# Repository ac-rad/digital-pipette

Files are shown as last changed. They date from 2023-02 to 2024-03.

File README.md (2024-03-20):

# Digital pipette


This repository contains CAD files and programs for [Digital pipette: Open hardware for liquid transfer in self-driving laboratories](https://doi.org/10.1039/D3DD00115F)

## Demo Video
https://user-images.githubusercontent.com/29328746/236104835-9dc766c4-92dd-4aab-9998-5ebd59588d73.mp4

## Bill of materials
| Item | Quantity | Description | Note |
| --- | --- | --- | --- |
| Linear actuator | 1 | Actuonix L16-100-63-6-R | https://www.actuonix.com/l16-100-63-6-r |
| DC 6V power supply | 1 | DC Linear Actuator Power Supply* | https://www.actuonix.com/dcpowersupply |
| Arduino | 1 | Arduino Uno Rev3** | https://store-usa.arduino.cc/products/arduino-uno-rev3 |
| Syringe | 1 | NORM-JECT Luer Solo (10 mL) | https://us.vwr.com/store/product/4646293/norm-ject-luer-lock-sterile-syringes-air-tite-products |
| Short screws & nuts | 3  | M3 10 mm screws and M3 nuts were used | |
| Long screw & nut | 1 | M3 20 mm screw and M3 nut were used | |

Basic electronic Parts to build a circuit (e.g. breadboard, cables, soldering iron, etc.) are not included in the list.

\* Any other DC 6V power supply should work.

** Any other Arduino-compatible boards should work.

## Electric circuit


Although it is not drawn explicitly, please make sure that the GND of Arduino and DC 6V power supply are connected.

### Example setup
You can connect with Arduino, the linear actuator, and the 6V power using jumper wires and alligator cables. This setup works for development, but it is not recommended for production since cables get easily disconnected.



Soldering wires is recommended for production to make connections more stable. My example using a PCB prototyping board is shown below.



## Build instruction
### Step 1
Prepare items shown in the bill of materials. Print the [platform](https://github.com/ac-rad/digital-pipette/blob/main/design/stl/platform.stl), [plunger holder](https://github.com/ac-rad/digital-pipette/blob/main/design/stl/holder.stl) and [syringe cover](https://github.com/ac-rad/digital-pipette/blob/main/design/stl/cover.stl) with a 3D printer. The length of the linear actuator should be adjusted before building by using an Arduino and the provided code. A screwdriver and pliers are helpful to tighten screws.



### Step 2
Connect the linear actuator and the plunger holder with a short screw and a nut.

https://github.com/ac-rad/digital-pipette/assets/29328746/378bcaca-c717-46af-9cfb-5fd15bf9850b

### Step 3
Connect the linear actuator and the platform with plastic parts shipped with the actuator, screws (short and long), and nuts.

https://github.com/ac-rad/digital-pipette/assets/29328746/e1789dd6-4c45-4c4c-84f6-89d388aaab22

### Step 4
Connect the syringe plunger with the plunger holder. Fasten the syringe with the platform and the syringe cover.

https://github.com/ac-rad/digital-pipette/assets/29328746/42ebc0b9-3168-43e8-8522-d95415921b36

### Step 5
Connect the linear actuator with the electric circuit.

## Source code
[src](https://github.com/ac-rad/digital-pipette/tree/main/src) directory contains an example code to operate the digital pipette.
- `pipette.ino` is an example Arduino sketch
- `controller.py` is an example Python code to send commands from PC to the Arduino

## Citation
If you find this useful in your research, please consider citing as below.

```
@article{yoshikawa2023digital,
  author = "Yoshikawa, Naruki and Darvish, Kourosh and Vakili, Mohammad Ghazi and Garg, Animesh and Aspuru-Guzik, Al{\'a}n",
  title = "Digital pipette: open hardware for liquid transfer in self-driving laboratories",
  journal = "Digital Discovery",
  year = "2023",
  volume = "2",
  issue = "6",
  pages = "1745-1751",
  publisher = "Royal Society of Chemistry",
  doi = "10.1039/D3DD00115F"
}
```

## License
The pipette is licensed under the [Creative Commons Attribution 4.0 International License][cc-by].

[][cc-by]

[cc-by]: http://creativecommons.org/licenses/by/4.0/
[cc-by-image]: https://i.creativecommons.org/l/by/4.0/88x31.png

The source code is licensed under the MIT license.

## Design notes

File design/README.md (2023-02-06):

# Design files for digital pipette
- `f3d/` contains Fusion 360 model in F3D format
- `stl/` contains 3D model in STL format.

`platform_upper` and `platform_bottom` are designed for 3D printers with small printable area.

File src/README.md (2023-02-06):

# Souce code for the digital pipette

- `pipette.ino` is an Arduino sketch
- `controller.py` is an Python example to send commands from PC

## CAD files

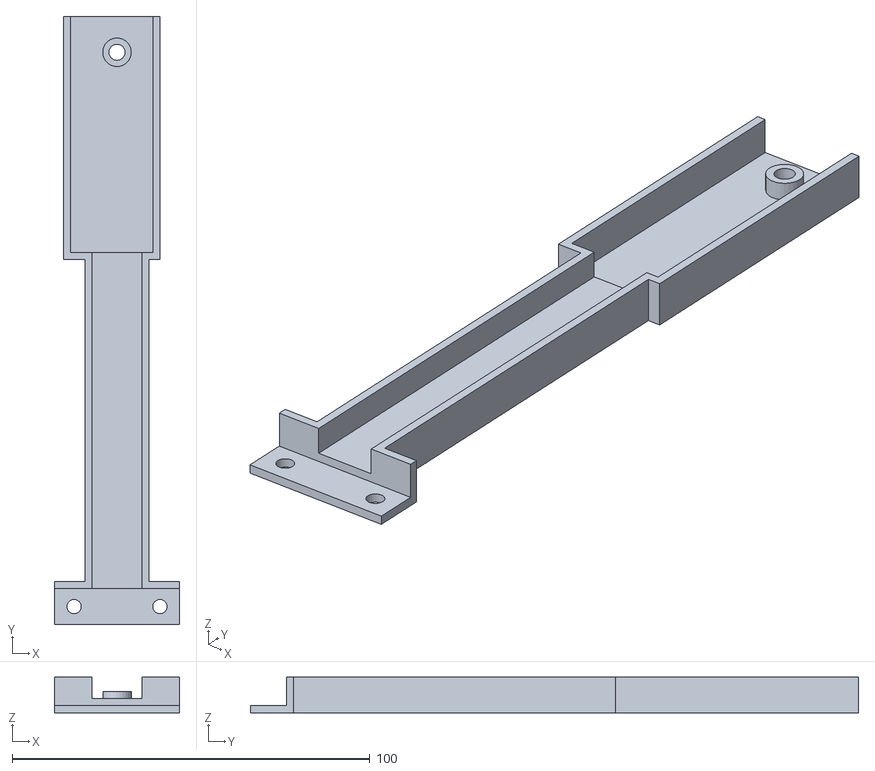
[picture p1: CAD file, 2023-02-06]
design/stl/platform_upper.stl
35.0 x 170.0 x 10.0

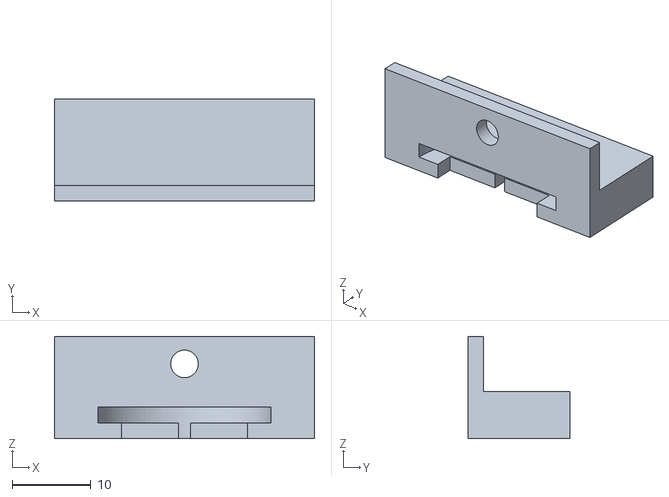
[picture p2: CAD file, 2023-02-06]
design/stl/holder.stl
33.0 x 13.0 x 13.0

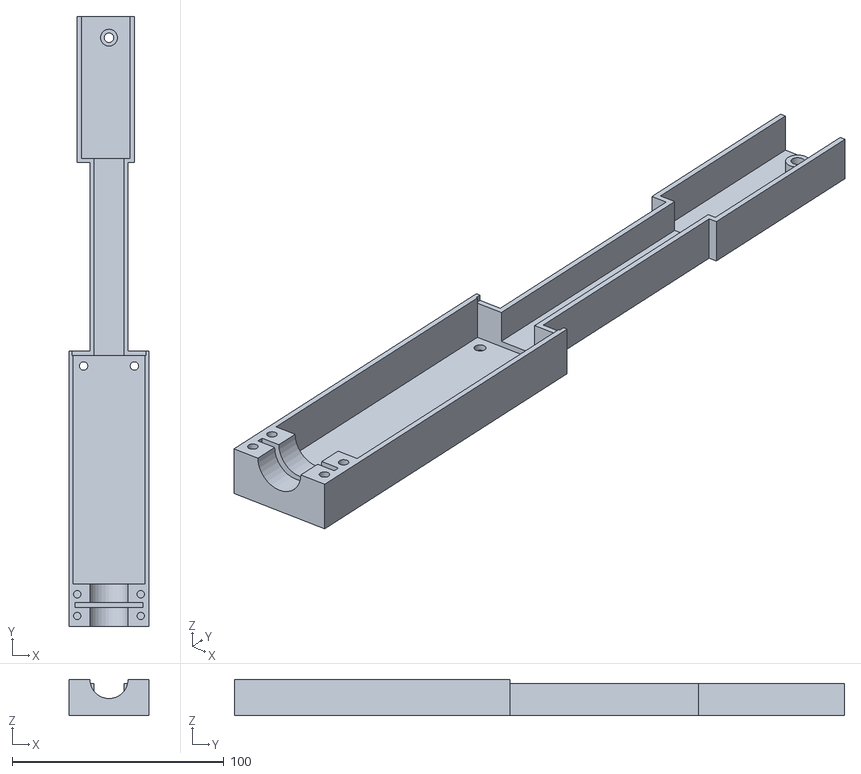
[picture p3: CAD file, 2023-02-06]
design/stl/platform.stl
38.0 x 288.0 x 17.0

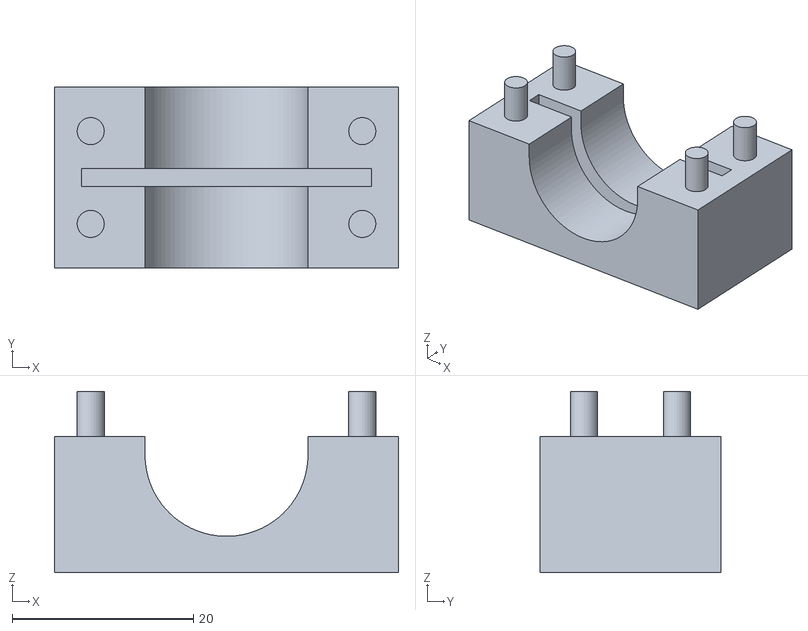
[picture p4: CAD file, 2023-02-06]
design/stl/cover.stl
38.0 x 20.0 x 20.0

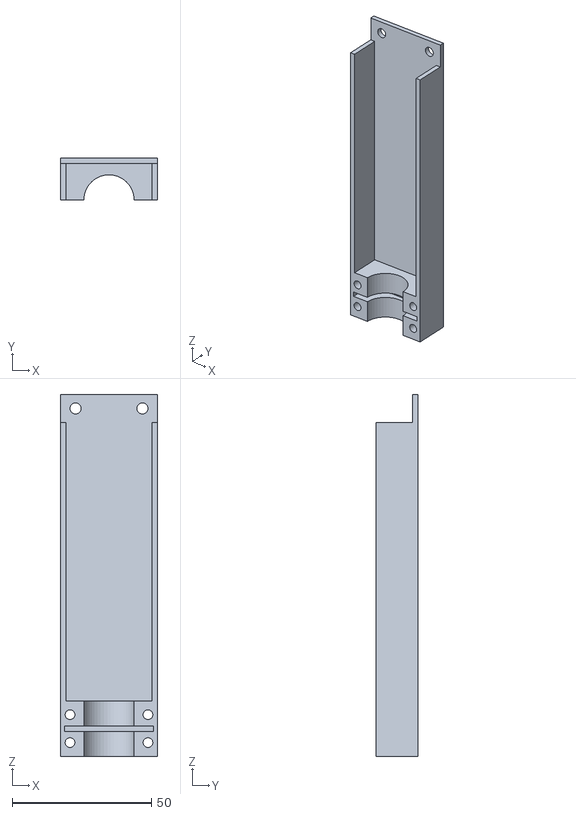
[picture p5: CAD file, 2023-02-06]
design/stl/platter_bottom.stl
35.0 x 15.0 x 130.0

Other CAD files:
design/f3d/cover.f3d
design/f3d/holder.f3d
design/f3d/platform.f3d
design/f3d/platform_bottom.f3d
design/f3d/platform_upper.f3d

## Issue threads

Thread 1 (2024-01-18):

### ISSUE TITLE
How to extend the linear actuator prior to assembly?

### ISSUE THREAD

**Issue by sgbaird** [ac-rad/digital-pipette#1]
It shipped in the fully retracted state, and it seems to be geared down at a high enough ratio that I can't pull it out by hand. Do you suggest running the code before assembling the hardware? Something else?

**Comment by sgbaird** [comment]
Response from @n-yoshikawa:
> I usually run the code before assembly

**Comment by n-yoshikawa** [comment]
I update the documentation to clarify this. Thank you for pointing it out!
